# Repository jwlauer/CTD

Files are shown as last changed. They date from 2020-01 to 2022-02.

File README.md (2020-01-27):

# CTD
This repository includes code for developing a simple conductivity, temperature, depth (CTD) sensor using a pyboard, a MS5803-05 pressure sensor, a Littlefuse PS103J2 NTC thermistor, and micropython. 

Code is provided for 2-pole and 4-pole versions of the conductivity sensor.  The methods for interacting with and reading conductivity sensors of these configurations are defined in the conductivity2pole.py and conductivity4pole.py files, respectively.  Both utilize a pseudo-AC method for making the conductivity measurement that involves raising one pole to a voltage near 3.3V, grounding the other, taking an ADC reading, switching the 3.3V and ground pins, and repeating a number of times. For conductivities under around 10,000 uS/m2, the two-pole sensor appears to work, but it exhibits significant drift for higher conductivities.  Since 10,000 uS/m2 is in the middle of the range of conductivities expected in many estuaries, the 4-pole version is recommended for use in those settings.  The 2-pole version may be appropriate in freshwater systems. 

The thermistor can be wired in parallel with the conductivity sensor, reducing the number of wires required for hooking it up.  However, if wired in parallel, it is necessary to operate in an alternating current mode in order to prevent polarization on the conductivity electrodes. The thermistor.py file can be used regardless of the wiring configuration. 

To install, modify the file logger_ctd.py to reflect whether you prefer to use the 2-pole or 4-pole configuration and to reflect your wiring configuration. All pin definitions are specified in that file. The 4-pole version of the code requires the use of four ADC pins, two pins for powering the conductivity sensor, two pins for powering the MS5803-05 pressure sensor, and two pins for I2C communication with the MS5803-05 pressure sensor. The two-pole version requires two fewer pins.  To use the code, after making any required modifications, copy all files to an SD card and insert into the SD slot on a pyboard. The program will then run automatically. 

The logging file places the device in the low-power wait state (not deep sleep) that results in an average current consumption of around 1-2 mA. An LED flashes periodically during operation. The logging file can be modified by placing the device in deep sleep, but this proved unreliable because the device sometimes did not mount the SD card upon waking, thereby terminating the logging cycle.  This could be addressed in a future version by calling the pyboard's watchdog timer. There are notes in logger_ctd.py indicating where this can be enabled--but the main loop in that program would need to be modified.

The sensor must be calibrated using a solution of known conductivity.  Because the response is not linear across the range of conductivities expected in an estuarine setting, the calibration process needs to include multiple points. A calibration curve can then be fit to these observations. Python code is provided in the "calibration" folder for doing the curve fitting. 

Tested with MicroPython 1.10 on a pyboard v1.1.

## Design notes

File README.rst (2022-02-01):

Overview
============

This repository includes code for developing a simple conductivity, temperature, depth (CTD) sensor using a `Pyboard <https://store.micropython.org/product/PYBv1.1H>`__, a `MS5803-05BA <https://www.amsys-sensor.com/products/pressure-sensor/ms5803-series-digital-absolute-pressure-sensors-up-to-1-2-5-7-14-30-bar/>`__ pressure sensor, a `Littlefuse PS103J2 <https://www.littelfuse.com/~/media/electronics/datasheets/leaded_thermistors/littelfuse_leaded_thermistors_interchangeable_thermistors_standard_precision_ps_datasheet.pdf.pdf>`__ NTC thermistor, and `Micropython <https://micropython.org/>`__.  It contains Gerber files for a minimal circuitboard for mounting the MS5803 sensor and for simplifying wiring for the electrical conductivity sensor.  It also contains STL files for 3D printing an optional housing for the electrodes and/or MS5803 sensor. 

Full documentation is avilable at https://ctd.readthedocs.io/en/latest/index.html.

Principle of Operation
----------------------

The electrical conductivity sensor requires no components other than a few resistors and either two or four electrodes.  Code is provided for both the 2-pole and 4-pole versions.  Both utilize a pseudo-AC method for making the electrical conductivity (EC) measurement that involves raising one electrode to a voltage near 3.3V using a digitial IO of the Pyboard, placing the other at a low digital output (close to 0V), taking an ADC reading (from which current through the circuit can be computed), and then switching the 3.3V and ground pins and repeating a number of times. A similar method is described in `NIST Special Publication 260-142 <https://www.nist.gov/system/files/documents/srm/260-142-2ndVersion.pdf>`__. For conductivities under around 10,000 μS/cm, the two-pole sensor appears to work, but it exhibits significant drift for higher conductivities.  Since 10,000 μS/cm is in the middle of the range of conductivities expected in many estuaries and is well below conductivities expected in marine environments, the 4-pole version is recommended for use in those settings.  The 2-pole version may be appropriate in freshwater systems. 

Depth is estimated based on pressure measurements made using the MS5803_05BA pressure sensor.  The MS5803 also provides a temperature signal, but provisions are also made for using an NTC thermistor for temperature measurements. The thermistor can be wired in parallel with the conductivity sensor, reducing the number of wires required for assembly.  However, if wired in parallel, thermistor measurements must be made very quickly in order to prevent polarization. 

Use of Code
-----------

To install, modify the file logger_ctd.py to reflect the EC configuration (two pole or four pole) and temperature measurement source. All pin definitions are specified in that file. The four-pole version of the code requires the use of four ADC pins, two pins for powering the conductivity sensor, two pins for powering the MS5803-05 pressure sensor, and two pins for I2C communication with the MS5803-05 pressure sensor. The two-pole version requires two fewer pins.  After making any required modifications, copy all files to the microcontroller. If using a Pyboard, all that is necessary is to copy the files to an SD card and insert into the SD slot. The program will then run automatically when the board is reset and will save the datalog file to the SD card. 

While the code has not been tested on other microcontrollers, it should be useable on any microcontroller with at least three accurate ADC pins (four if using the NTC thermistor). 

Deployment
----------

The logging file places the device in the low-power wait state (not deep sleep) that results in an average current consumption of around 1-2 mA. An LED flashes periodically during operation. The logging file can be modified to place the device in deep sleep, but this proved unreliable because the device sometimes did not mount the SD card upon waking, thereby terminating the logging cycle.  This could be addressed in a future version by calling the PyBoard's watchdog timer. There are notes in logger_ctd.py indicating where this can be enabled--but the main loop in that program would need to be modified.

Date and time are obtained from the Pyboard's Real Time Clock (RTC), which can be calibrated to an accuracy of better than several minutes per year. Setting and calibrating the clock is covered in the `Micropython docs <https://docs.micropython.org/en/latest/library/pyb.RTC.html#pyb-rtc>`__. The Pyboard also includes a "VBACK" pin for adding a backup battery. A CR2032 battery can keep the clock running for many months (probably years).  

Interpretation of Measurements
------------------------------

The sensor returns the apparent DC resistance between electrodes, computed using R = ΔV / I, where ΔV is the difference in voltage between the two sensing electrodes and I is the current estimated across the current sensing resistor. This resistance is computed for each direction of current flow. Each of these two apparent resistances are returned.  The average of these two apparent DC resistances is highly correlated with electrical conductivity. It also depends in part on the geometry of the electrodes, which can vary from sensor to sensor. This means that a separate calibration curve must be developed for each sensor using a solution of known conductivity.  The calibration curve is often represented as an inverse relationship between EC and R, EC = k/R, where R is the average resistance returned by the sensor (Ohms) and k is the cell constant of the sensor (cm \ :sup:`-1`) that is determined by calibration. Even stronger correlations can be obtained using a log-log fit between 1/R and EC. The code includes functions to simplify collection of calibration data points. 

Code was tested with Micropython 1.10 on a Pyboard v1.1 or Micropython v1.14 2021/04/01 unstable release (using rp2-pico-20210401-unstable-v1.14-128-gca3d51f12) on Raspberry Pi Pico 2040.

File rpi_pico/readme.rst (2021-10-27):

This folder includes the files necessary to use a Raspberry Pi Pico 2040 as the microcontroller in the CTD. Note that as of MicroPython v1.14 2021-02-27, power saving features are not enabled, so current use is relatively high (current on the order of 20-30 mA).  This is reduced in the code by reducing the processor frequency to a value that is as low as possible while waiting reducing current to about 4.5 mA on a Pico 2040.  Testing shows current is one or two mA higher on Adafruit 2040 boards. Modifications may be required in main.py once the pico 2040 power saving features are enabled in MicroPython.

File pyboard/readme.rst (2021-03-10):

This folder contains code for use with a pyboard. Because the pyboard includes many ADC pins, the code incorporates an NTC thermistor for measuring temperature, rather than using the somewhat less accurate MS5803.

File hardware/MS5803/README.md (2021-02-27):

This folder includes files that can be sent to a PCB manufacturer to produce the following breakout board.

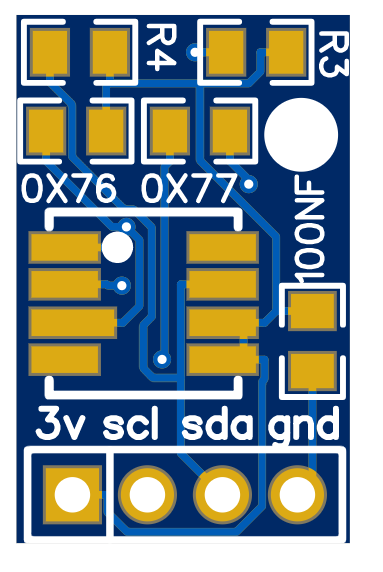
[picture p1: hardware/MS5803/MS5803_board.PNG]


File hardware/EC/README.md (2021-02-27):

This folder includes files that can be sent to a PCB manufacturer to produce the following breakout board.

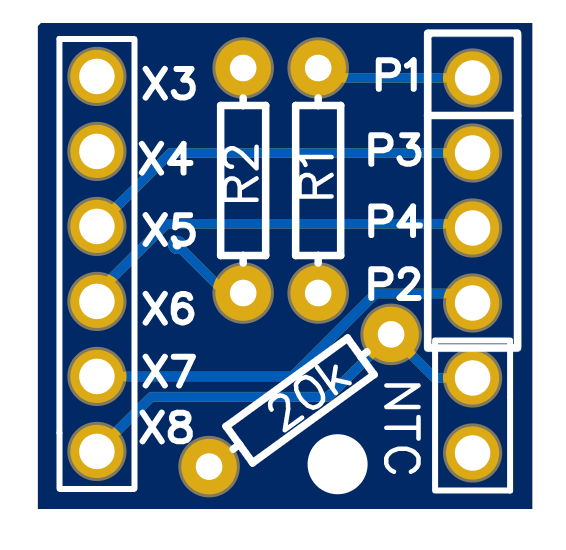
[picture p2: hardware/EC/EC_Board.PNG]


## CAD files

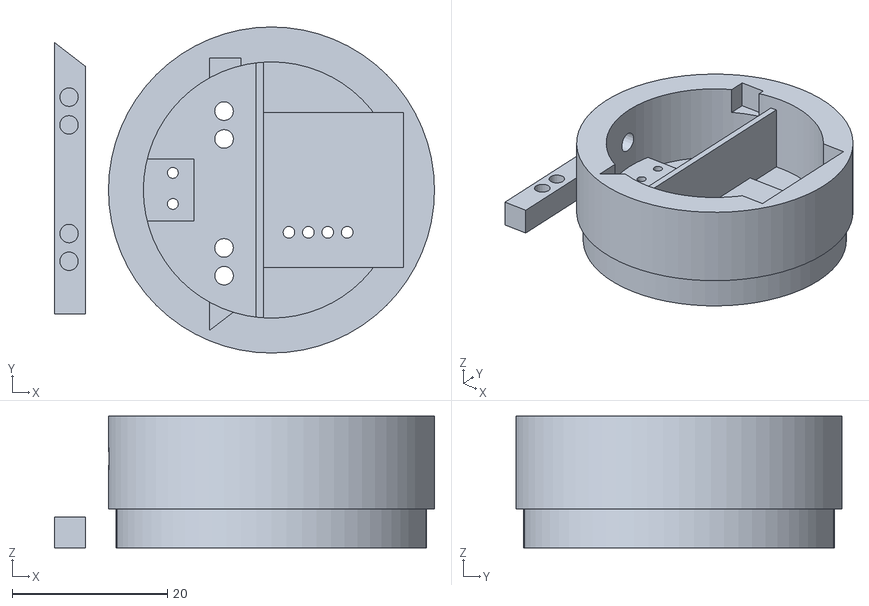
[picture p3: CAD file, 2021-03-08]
hardware/3d_print/CDT_Cap_1.5_inch_pipe.stl
49.0 x 42.0 x 17.0

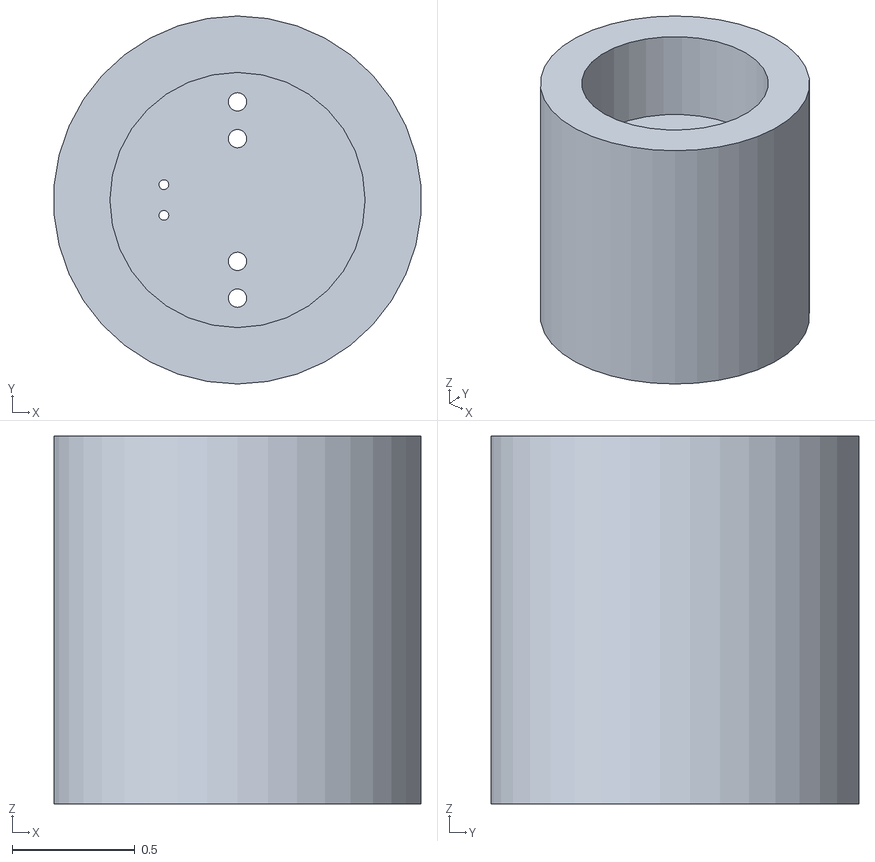
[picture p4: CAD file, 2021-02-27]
hardware/3d_print/ShortCap1inchPipe.stl
1.49 x 1.50 x 1.50

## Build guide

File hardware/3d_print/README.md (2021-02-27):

# 3d print files for the cap.

Files for printing a cap that works on 3/4 inch PVC and for 1.5 inch PVC pipe are available. The 1.5 inch version includes a spot to place an MS5803 sensor using the pcb developed as part of this project.

The version for the 1.5 inch pipe was developed in TinkerCAD and is available in the [TinkerCAD gallery](https://www.tinkercad.com/things/3EZ9vMYtAvf-cdtcap15inchpipe). 

Github includes a nice STL viewer, so click on any STL file in this folder to view.

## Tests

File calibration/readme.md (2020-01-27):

This folder includes files potentiall useful for calibration.

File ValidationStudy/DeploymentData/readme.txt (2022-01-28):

Files in this folder are data log files for deployment of sensors at North Winds Weir site from April 1 to April 5, 2021. Sensors were co-located
in the pool on the right bank at about -0.15 m MLLW for April 1-2, 3-4, and 4-5.  For April 2-3, sonde was located in main river at same elevation 
at entrance to pool, SU1 was located in pool about 1m depth, SU5 was on bank at mount of tidal channel, SU3 was in tidal channel on flat, and SU2 was 
in main river at footbridge at about 1 m depth.
  
The file datalogCTD_su4_processed.txt converts the time recorded by the Pico2040 to a real date/time.  There was a roughly 5 minute offset by the 
end of the deployment, so the time error was distributed into points proportional to the time the device had been on.  This results in both the
start date/time and the stop date/time matching the notes in the field book.

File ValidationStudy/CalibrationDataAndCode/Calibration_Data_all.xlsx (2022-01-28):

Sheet: SU5 3-17-21
Data collected 3/17/21 using KCl
Sensor SU5 run using Raspberry Pi Pico 2040
Trial | EXO EC(μS/cm) | EXO T (°C) | T (°C) | Kt | R1 | R2 | R | 1/R | 1/R (uS) | T offset | Error | Relative E | square relative error
1 | 45404.9 | 17.233 | 16.81 | 45404.9 | 2.94 | 19.75 | 11.345 | 0.08814455707 | 88144.55707 | 0.423 | 4797.627258 | 0.105663205 | 0.0111647129
1 | 45404.9 | 17.233 | 16.83 | 45404.9 | 3.79 | 21.83 | 12.81 | 0.07806401249 | 78064.01249 | 0.403 | -908.0707012 | -0.01999939877 | 0.0003999759512
1 | 45404.9 | 17.233 | 16.85 | 45404.9 | 2.68 | 21.44 | 12.06 | 0.08291873964 | 82918.73964 | 0.383 | 1840.328694 | 0.04053149978 | 0.001642802474
2 | 25864.4 | 18.835 | 17.26 | 25864.4 | 11.73 | 29.18 | 20.455 | 0.04888780249 | 48887.80249 | 1.575 | 2088.068318 | 0.08073136503 | 0.006517553299
2 | 25864.4 | 18.835 | 17.34 | 25864.4 | 11.74 | 31.41 | 21.575 | 0.04634994206 | 46349.94206 | 1.495 | 646.3272789 | 0.0249890691 | 0.0006244535746
2 | 25864.4 | 18.835 | 17.35 | 25864.4 | 12.48 | 31.09 | 21.785 | 0.04590314437 | 45903.14437 | 1.485 | 392.4514303 | 0.01517342101 | 0.000230232705
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

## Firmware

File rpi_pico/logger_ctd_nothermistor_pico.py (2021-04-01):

import machine
import time
from machine import Pin, ADC
import pressure
import math
import array as arr
#import thermistor_ac
import conductivity4pole_pico
import time

def log(t):
    """ A function for logging data to file at a regular interval.

    The function saves a line of text at each interval representing conductivity, temperature,
    pressure. The device then goes into standby mode for interval t.  After interval t, the
    device awakes as if from a hard reset.  The function is designed to be called from
    main.py. Puts device in standby mode upon completion.

    Parameters
    ----------
    t: int
        logging interval (seconds)
    
    Example
    -------
    To log data at 30 second intervals, save the following two lines as main.py
	
    >>> import logger_ctd_nothermistor_pico as logger
    >>> logger.log(30)
	
    Note
    ----
    For more robust logging, the lines related to the watchdog timer can be enabled
    by removing the comments.  However, once the watchdog timer is set, it will automatically
    reset the board after the watchdog timer interval unless the timer is fed. This ensures
    that the board will continue to log even if an error is encountered, but it can
    cause unexpected results if the user wishes to interact with the board over serial.

    """
    
    green = Pin(25, Pin.OUT)   
    green.value(1)

    #wait 10 seconds to allow user to jump in
    time.sleep(10)
    green.value(0)
    def flash(n,t):
        for i in range(n):
            green.value(1)
            time.sleep(t)
            green.value(0)
            time.sleep(t)
            
    #write file header
    outputtxt = 'time(s),R1(ohm),R2(ohm),temp(C),pres(mbar)\r\n'
    try:
        f = open('datalogCTD.txt','a')
        f.write(outputtxt)
        f.close()
    except:
        #short flash led if fails to write
        flash(20,0.2)
        
    start_time = time.time()   
    
    while True:
        #single flash LED to let user know reading is being taken
        machine.freq(125000000)
        flash(1,0.25)
        
        log_time = start_time + t
        start_time = log_time
        
        #define conductivity sensor 
        gpio1 = Pin(19, Pin.OUT)  #connected directly to electrode
        gpio2 = Pin(20, Pin.OUT)  #connected to resistor connected to electrode
        adc1 = ADC(26)          #connected to middle pole not adjacent to
        adc2 = ADC(27)          #connected to middle pole adjacent to resistor
        adc3_current = ADC(28)
        #adc_therm = ADC(28)        #Not used in pico 2040, but may be available on other 2040 boards
        con_resistance = 250
        #therm_resistance = 20000
        cell_const = 1    
        b = 0     
        conductivity_sensor = conductivity4pole_pico.cond_sensor(gpio1,gpio2,adc1,adc2,adc3_current,con_resistance,cell_const,b)

        #define pressure sensor in Pressure.py.  
        pres_power = Pin(18, Pin.OUT)
        #pres_gnd = Pin(19, Pin.OUT_PP)   #not needed if ground pin directly connected to gnd
        i2c = machine.I2C(0, scl=Pin(17), sda=Pin(16), freq = 100000)
                    
        #read values from sensors
        try:
            [r1, r2, icount1, probe3count1, probe4count1, icount2, probe3count2, probe4count2] = conductivity_sensor.measure(n = 50)
        except:
            [r1, r2, icount1, probe3count1, probe4count1, icount2, probe3count2, probe4count2] = [-999,-999,-999,-999,-999,-999,-999,-999,-999,-999]
        
        try:
            [pres, ctemp] = pressure.MS5803(i2c, pres_power)
        except:
            pres = -999
            ctemp = -999
            print('Pressure reading failed')
            flash(5,.2)
        
        #write results to file
        #outputtxt = ('%s/%s/%s,%s:%s:%s,' % (datetime[0], datetime[1], datetime[2], datetime[4], datetime[5], datetime[6]))
        outputtxt = ('%s,' % (start_time-1609459241))
        outputtxt += ('%5.2f,%5.2f,' % (r1, r2))
        outputtxt += ('%5.2f,' % ctemp)
        outputtxt += ('%5.1f\r\n' % pres)
        print (outputtxt)
        try:
            f = open('datalogCTD.txt','a')
            f.write(outputtxt)
            f.close()
            flash(5,0.05)
        except:
            flash(20,0.2)
        
        machine.freq(10000000)
        while time.time() < log_time:          
            flash(1, 0.05)
            green.value(0)
            time.sleep(1)
            #machine.lightsleep(1)
            

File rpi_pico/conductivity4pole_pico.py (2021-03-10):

"""A four-pole conductivity sensor containing a thermistor.

"""

import machine
from machine import Pin, ADC
import time
import math
import array as arr

class cond_sensor:
    """A class for interacting with a four-pole conductivity sensor and thermistor.

    Performs measurement using the analog to digial converter
    to read values of voltage drop across the two inner electrodes 
    (when excited by a square wave applied to two outer electrodes) 
    and to read values from the thermistor.  Also includes methods for
    converting readings to physical values, based on calibration
    parameters specified when instantiated. Requires following import statements::
	
        import machine
        from machine import Pin, ADC
        import time
        import math
        import array as arr
    
    Parameters
    ----------
    gpio1 : :obj:'machine.Pin(pinid, Pin)'
        Power/ground pin connected directly to current balancing resistor R1
    gpio2 : :obj:'machine.Pin(pinid, Pin)'
        Power/ground pin connected to current measuring resistor R1
    adc1 : :obj:'machine.ADC(pinid)'
        ADC pin connected to electrode 3 (sensing pole farthest from current measuring resistor)
    adc2 : :obj:'machine.ADC(pinid)'
        ADC pin connected to electrod 4 (sensing pole closest to current measuring resistor)
    adc3_current : :obj:'machine.ADC(pinid)'
        ADC pin connected between conductivity resistor and conductivity electrode
    con_resistance: float
        Resistance (ohm) of current measuring resistor 
    cell_const : float
        Cell constant (1/cm), found through calibration
    b : float
        Intercept in linear calibration equation
       
    Attributes
    ----------     
    resistance1 : float
        Apparent resistance computed from count1 
    resistance2 : float
        Apparent resistance computed from count2
    T : float
        Temperature (degrees C)
    k : float
        Conductivity (uS/cm)
    S : float
        Salinity
    
    Example
    -------
    >>> import conductivity4pole_pico
    >>> gpio1 = Pin(19,Pin.OUT)
    >>> gpio2 = Pin(20,Pin.OUT)
    >>> adc1 = ADC(26)
    >>> adc2 = ADC(27)
    >>> adc3_current = ADC(28)
    >>> res = 250
    >>> cell_const = 1
    >>> b = 0
    >>> Sensor1 = conductivity4pole_pico.cond_sensor(gpio1,gpio2,adc1,adc2,adc3_current,res,cell_const,b)
    >>> Sensor1.calibrate()
    >>> #run external calibration to get cell constant and intercept b
    >>> Sensor1.cell_const = 1 #enter correct values here
    >>> Sensor1.b = 0
    >>> Sensor1.measure()

    """
    
        
    def __init__(self, gpio1, gpio2, adc1, adc2, adc3_current, con_resistance, cell_const, b):
        
        self.gpio1 = gpio1
        self.gpio2 = gpio2
        self.adc1 = adc1
        self.adc2 = adc2
        self.adc3_current = adc3_current
        self.con_resistance = con_resistance
        self.cell_const = cell_const
        self.b = b
        self.gpio1.low()
        self.gpio2.low()

    def conductivity(self,r2,cell_const,b):
        """Apply the sensor-specific conductivity calibration equation.

        Compute a sensor-specific value of conductivity from measured cell resistance
        and calibration values. Returns a sensor-specific value of conductivity
        Using the linear relationship between k and calibration data
        Parameters are sensor-specific parameters that must
        be found by calibration.   
        
        Parameters
        ----------
        r2 : float
            Apparent resistance (ohms) of the solution when the power is applied to electrode connected 
            directly to the power pin.
        cell_const : float
            cell constant (1/cm). Equivalent to slope of d(EC)/dR. 
        b : float
            intercept (micro S/cm) in equation EC = 1/(cell_c*R2)+b 

        Returns
        -------
        float
            Calibrated conductivity
                
        """
        k = 1/(cell_const*r2) + b
        return k   

    def salinity(self,T,k):
        """Salinity computation for seawater and estuarine water.      
        Salinity computation is from Miller, Bradford, and Peters,
        USGS Water Supply Paper 2311.    
        
        Parameters
        ----------      
        T: float
            Temperature (degrees C)
        k: float
            Conductance (mS/cm) 

        Returns
        -------
        float
            Salinity (parts per thousand)
                
        """
        B0 = 0.13855E1
        B1 = -0.46485668E-1
        B2 = 0.14887785E-2
        B3 = -0.63083433E-4
        B4 = 0.25144517E-5
        B5 = -0.59600245E-7
        B6 = 0.57778085E-9
        K = B0 + B1*T + B2*T**2 + B3*T**3 + B4*T**4 + B5*T**5 + B6*T**6
        A = 0.36996/(k**(-1.07)-0.7464E-3)
        chlorinity = A * K
        salinity = 1.80655 * chlorinity
        return salinity
            
    def k25(self,k,T):
        """
        Calculate conductivity at standard temperature of 25C, for KCl or fresh water (not seawater).
        
        Given by USGS Water Supply Paper and Pawlowicz 2008.
        
        """
        return k*(1/(1+0.0191*(T-25)))
    
    def TDS(self,k25):
        """
        Calculate total dissolved solids from conductivity at 25C, from Pawlowicz 2008, which says the coefficient varies widely.
        """
        TDS = 0.65*k25
        return TDS

    def measure(self, printflag = False,n = 12,on1 = 0, off1 = 0, on2 = 0, off2 = 0): #take a reading
        """
        Performs a measurement of conductivity across a four-pole probe.
        
        Parameters
        ----------
        saveflag: boolean, optional
            Flag to determine if output is saved for calibration, default false
        n: int, optional
            Number of adc readings to take for the measurement, default = 12
        on1: int, optional
            time in microseconds that power pin 1 is on before taking a reading, default = 0
        off1: int, optional
            time in microseconds that power pin 1 is turned off before turning on power pin, default = 0
        on2: int, optional
            time in microseconds that power pin 2 is on before taking a reading, default = 0
        off2: int,optional
            time in microseconds that power pin 2 is turned off before turning on power pin, default = 0
            
        Returns
        -------
        resistance1 : float
            Apparent resistance computed using normal polarity.
        resistance2 : float
            Apparent resistance computed using reverse polarity.
        temperature : float
            Temperature (degrees C)
        conductivity : float
            Conductivity.
                            
        Note
        ----
        Also sets the value for temperature, conductivity, counts, and resistances
        """
        
        #pre-allocate arrays for counts to be read into
        imeas1 = arr.array('l',[0]*n)
        imeas2 = arr.array('l',[0]*n)
        p3meas1 = arr.array('l',[0]*n)
        p3meas2 = arr.array('l',[0]*n)
        p4meas1 = arr.array('l',[0]*n)
        p4meas2 = arr.array('l',[0]*n)


        starttime = time.ticks_us()
        for i in range(n):
            self.gpio1.high()
            time.sleep_us(on1)
            imeas1[i] = (self.adc3_current.read_u16() >> 4)
            p3meas1[i] = (self.adc1.read_u16() >> 4)
            p4meas1[i] = (self.adc2.read_u16() >> 4)
            self.gpio1.low()
            time.sleep_us(off1)
            
            self.gpio2.high()
            time.sleep_us(on2)
            imeas2[i] = (self.adc3_current.read_u16() >> 4)
            p3meas2[i] = (self.adc1.read_u16() >> 4)
            p4meas2[i] = (self.adc2.read_u16() >> 4)
            self.gpio2.low()
            time.sleep_us(off2)

        endtime = time.ticks_us()
        elapsed_time = endtime - starttime            

        #pre-allocate arrays for current, voltage drop across poles, and resistance, for flow each direction
        i1 = arr.array('f',[0]*n)
        i2 = arr.array('f',[0]*n)
        V1 = arr.array('f',[0]*n)
        V2 = arr.array('f',[0]*n)
        R1 = arr.array('f',[0]*n)
        R2 = arr.array('f',[0]*n)

        #compute current, voltage, and resistance for each sample (do outside sampling loop to maintain sampling timing)
        for i in range(n):
            try:
                i1[i] = imeas1[i] / 4095 * 3.3 / self.con_resistance 
                i2[i] = (3.3 - imeas2[i] / 4095 * 3.3) / self.con_resistance
                V1[i] = (p3meas1[i] - p4meas1[i])/4095 * 3.3
                V2[i] = (p4meas2[i] - p3meas2[i])/4095 * 3.3
                R1[i] = V1[i]/i1[i]
                R2[i] = V2[i]/i2[i]
            except:
                R1[i] = -999999
                R2[i] = -999999
                print('Error in resistance computation')
        
        #clean data by sampling middle two quartiles       
        upper_index = math.ceil(3*n/4)
        lower_index = math.floor(n/4)
        sampled_length = (upper_index - lower_index)
        self.resistance1 = sum(sorted(R1)[lower_index:upper_index])/sampled_length
        self.resistance2 = sum(sorted(R2)[lower_index:upper_index])/sampled_length
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

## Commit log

2021-02-21 Added pressure/temperature logger
2021-02-22 Updated lighting on pressure/temperature logger
2021-02-27 Added Gerber Files for EC Board
    [Gerber_BoardOutline.GKO, Gerber_BottomLayer.GBL, Gerber_BottomSilkLayer.GBO, Gerber_BottomSolderMaskLayer.GBS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]
2021-02-27 Added Gerber files for MS5803
    [Gerber_BoardOutline.GKO, Gerber_BottomLayer.GBL, Gerber_BottomSolderMaskLayer.GBS, Gerber_Drill_NPTH.DRL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]
2021-02-27 Added caps for several pipe sizes
    [CDT_Cap_1.5_inch_pipe.stl, ShortCap1inchPipe.stl]
2021-02-27 Delete CDT_Cap.stl
    Removed version with misaligned holes.
    [CDT_Cap.stl]
2021-03-08 Fixed air escape hole
    [CDT_Cap_1.5_inch_pipe.stl]
2021-03-10 Made pin assignments consistent with drawings
2021-03-10 Updated pin definitions and oversampling rate
2021-03-14 Changed LED Flash Patterns
2021-03-16 Added missing pressure.py file
2021-04-01 Reduced frequency while sleeping to save power
2021-10-27 Added current measurement
2022-01-28 Calibration and deployment data added
    [Calibration_Data_all.xlsx]
